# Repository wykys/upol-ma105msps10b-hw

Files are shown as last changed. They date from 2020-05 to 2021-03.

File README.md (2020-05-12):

# Multikanálový analyzátor 105 MSPS 10b

Vývoj hardware pro multikanálovou analýzu.

## Datasheets
Technická dokumentace používaná k vývoji.
### FPGA Xilinx 7 Series
- [Vivado Design Suite User Guide](https://www.xilinx.com/support/documentation/sw_manuals/xilinx2016_2/ug908-vivado-programming-debugging.pdf)
- [7 Series FPGAs Data Sheet: Overview](https://www.xilinx.com/support/documentation/data_sheets/ds180_7Series_Overview.pdf)
- [DC and AC Switching Characteristics](https://www.xilinx.com/support/documentation/data_sheets/ds189-spartan-7-data-sheet.pdf)
- [7 Series FPGAs Configuration User Guide](https://www.xilinx.com/support/documentation/user_guides/ug470_7Series_Config.pdf)
- [Using SPI Flash with 7 Series FPGAs](https://www.xilinx.com/support/documentation/application_notes/xapp586-spi-flash.pdf)
- [Spartan-7 FPGA Configuration with SPI Flash and Bank 14 at 1.35V](https://www.xilinx.com/support/documentation/application_notes/xapp1313-spartan-spi-config.pdf)
- [7 Series FPGAs SelectIO Resources User Guide](https://www.xilinx.com/support/documentation/user_guides/ug471_7Series_SelectIO.pdf)
- [7 Series FPGAs PCB Design Guide](https://www.xilinx.com/support/documentation/user_guides/ug483_7Series_PCB.pdf)
- [7 Series FPGAs Packaging and Pinout](https://www.xilinx.com/support/documentation/user_guides/ug475_7Series_Pkg_Pinout.pdf)

### Další dokumenty
- [Přehled logických obvodů ST](https://www.mouser.com/catalog/supplier/library/pdf/STLogic.pdf)
- [Zakončování LVCMOS](https://www.idt.com/eu/en/document/apn/953-quick-guide-output-terminations)
- [USB specifikace](https://www.silabs.com/documents/public/application-notes/AN0046.pdf)

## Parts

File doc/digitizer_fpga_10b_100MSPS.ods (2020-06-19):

Reference | Quantity | Value | Footprint | Datasheet | Link
C1 C2 C11 C12 C15 C16 C27 C28 C33 C35 C36 C45 C54 C57 C58 C61 C66 C78 C79 C80 C81 C83 C85 C86 C87 C98 C102 | 27 | 4u7 | Capacitor_SMD:C_0402_1005Metric | ~
C10 C19 C26 C43 C55 C63 C64 C65 C68 | 9 | 1u | Capacitor_SMD:C_0402_1005Metric | ~
C3 C4 C8 C9 C13 C14 C17 C18 C23 C24 C25 C32 C34 C37 C38 C39 C40 C41 C42 C44 C46 C47 C49 C50 C53 C56 C59 C60 C62 C67 C69 C70 C71 C72 C84 | 35 | 100n | Capacitor_SMD:C_0402_1005Metric | ~
C30 C31 | 2 | 2u2 | Capacitor_SMD:C_0402_1005Metric | ~
C5 C6 C20 C21 C48 C108 | 6 | 1n | Capacitor_SMD:C_0402_1005Metric | ~
C51 C52 | 2 | 47p | Capacitor_SMD:C_0402_1005Metric | ~
C7 C22 C29 | 3 | 47u/16V | Capacitor_Tantalum_SMD:CP_EIA-7343-31_Kemet-D | ~
C73 C74 C75 C76 C77 C82 C88 C93 | 8 | 47u | Capacitor_SMD:C_0402_1005Metric | ~
C89 C90 C91 C92 C94 C95 C96 C97 C99 C100 C101 C103 C104 C105 C106 C107 | 16 | 470n | Capacitor_SMD:C_0402_1005Metric | ~
D1 | 1 | AS3BJ-M3/52T | Diode_SMD:D_SMB | ~
D2 | 1 | PTVS3V3P1UP.115 | Diode_SMD:D_SOD-128 | ~
D3 D4 D5 D6 | 4 | BAT20JFILM | Diode_SMD:D_SOD-323 | ~
D7 D8 D9 D10 D11 D12 D13 D14 D15 | 9 | RED | LED_SMD:LED_0805_2012Metric | ~
FB1 | 1 | 742792515 | Inductor_SMD:L_1812_4532Metric | ~
J1 | 1 | POWER | Connector_Phoenix_MC:PhoenixContact_MC_1,5_2-G-3.5_1x02_P3.50mm_Horizontal | ~
J2 | 1 | SWD_01X06 | Connector_PinHeader_2.54mm:PinHeader_1x06_P2.54mm_Vertical | ~
J3 | 1 | DEBUG_SPI | Connector_PinHeader_2.54mm:PinHeader_2x04_P2.54mm_Vertical | ~
J4 | 1 | USB_B_Mini | Connector_USB:USB_Mini-B_Lumberg_2486_01_Horizontal | ~
J5 | 1 | SMA | Connector_Coaxial:SMA_Samtec_SMA-J-P-X-ST-EM1_EdgeMount | ~
J6 | 1 | JUMPER_DFS/GAIN | Connector_PinHeader_2.54mm:PinHeader_2x04_P2.54mm_Vertical | ~
J7 | 1 | DEBUG_FPGA_GPIO | Connector_PinHeader_2.54mm:PinHeader_2x04_P2.54mm_Vertical | ~
J8 | 1 | DIGILENT_JTAG_HS2_01X06 | Connector_PinHeader_2.54mm:PinHeader_1x06_P2.54mm_Vertical | https://reference.digilentinc.com/_media/jtag_hs2:jtag-hs2_rm.pdf
JP1 | 1 | Jumper_FTDI_RST | Connector_PinHeader_2.54mm:PinHeader_1x02_P2.54mm_Vertical | ~
L1 | 1 | ETQP3M6R8KVP | Inductor_SMD:L_Bourns_SRN6045TA | ~
R1 R3 R4 R5 R14 R20 R21 R45 R121 R122 | 10 | 10k | Resistor_SMD:R_0603_1608Metric | ~
R11 | 1 | 2k87 | Resistor_SMD:R_0603_1608Metric | ~
R15 R16 R17 R18 R125 R126 R127 R128 | 8 | 220R | Resistor_SMD:R_0603_1608Metric | ~
R19 R22 R23 R27 R28 R29 R30 R31 R32 R33 R34 R35 R36 R48 R49 R50 R51 R52 R53 R54 R55 R56 R57 R58 R59 R60 R61 R62 R63 R64 R65 R66 R67 R68 R69 R70 R71 R72 R73 R74 R75 R76 R77 R78 R79 R80 R81 R82 R83 R84 R85 R86 R87 R89 R90 R91 R92 R93 R94 R95 R96 R97 R98 R99 R100 R101 R102 R103 R104 R105 R106 R107 R108 R109 R110 R111 R112 R113 R114 R115 R116 R117 | 82 | 47R | Resistor_SMD:R_0402_1005Metric | ~
R2 | 1 | 3k9 | Resistor_SMD:R_0603_1608Metric | ~
R24 R25 R26 R43 R44 R118 R119 R120 R129 R130 | 10 | 4k7 | Resistor_SMD:R_0603_1608Metric | ~
R37 R38 R39 R41 | 4 | 56R2 | Resistor_SMD:R_0603_1608Metric | ~
R40 R42 R46 R47 | 4 | 301R | Resistor_SMD:R_0603_1608Metric | ~
R6 | 1 | 1k13 | Resistor_SMD:R_0603_1608Metric | ~
R7 | 1 | 4k53 | Resistor_SMD:R_0603_1608Metric | ~
R8 R10 R12 | 3 | 3k57 | Resistor_SMD:R_0603_1608Metric | ~
R88 R123 R124 | 3 | 1k | Resistor_SMD:R_0603_1608Metric | ~
R9 R13 | 2 | 1k15 | Resistor_SMD:R_0603_1608Metric | ~
SW1 | 1 | RST | Button_Switch_SMD:SW_SPST_CK_RS282G05A3 | ~
SW2 | 1 | PROG | Button_Switch_SMD:SW_SPST_CK_RS282G05A3 | ~
U1 | 1 | LM3880MF-1AA | Package_TO_SOT_SMD:SOT-23-6 | http://www.ti.com/lit/ds/symlink/lm3880.pdf | https://cz.mouser.com/ProductDetail/Texas-Instruments/LM3880MF-1AA?qs=QbsRYf82W3Fl%2Fq3cHZXlFw%3D%3D
U10 | 1 | ADA4930-1 | Package_CSP:LFCSP-16-1EP_3x3mm_P0.5mm_EP1.7x1.7mm | https://www.analog.com/media/en/technical-documentation/data-sheets/ADA4930-1_4930-2.pdf | https://cz.mouser.com/ProductDetail/Analog-Devices/ADA4930-1YCPZ-R7?qs=BpaRKvA4VqGLtX2TPWl0aQ%3D%3D
U11 | 1 | IS61WV12816EDBLL-10TLI | Package_SO:TSOP-II-44_10.16x18.41mm_P0.8mm | http://www.issi.com/WW/pdf/61-64WV12816EDBLL.pdf | https://cz.mouser.com/ProductDetail/ISSI/IS61WV12816EDBLL-10TLI?qs=9hm%252BDT1Jr7wdTeyW8VsKuw%3D%3D
U12 | 1 | TLV431ACDBZR | Package_TO_SOT_SMD:SOT-23 | http://www.ti.com/lit/ds/symlink/tl431.pdf | https://cz.mouser.com/ProductDetail/Texas-Instruments/TLV431ACDBZR?qs=m96fseALk3UFqurlruAFnw%3D%3D
U13 | 1 | AD9214-105 | Package_SO:SSOP-28_5.3x10.2mm_P0.65mm | https://www.analog.com/media/en/technical-documentation/data-sheets/AD9214.pdf | https://cz.mouser.com/ProductDetail/Analog-Devices/AD9214BRSZ-105?qs=%2FtpEQrCGXCwwKyKT%252BwKAAg%3D%3D
U14 | 1 | XC7S15-FTGB196 | Package_BGA:Xilinx_FTGB196 | https://www.xilinx.com/support/documentation/data_sheets/ds180_7Series_Overview.pdf | https://cz.mouser.com/ProductDetail/Xilinx/XC7S15-2FTGB196I?qs=unwgFEO1A6uXTG1xGkfbTw%3D%3D | zkontrolovat pouzdro
U15 | 1 | IS25LP064A-JKx | Package_SON:WSON-8-1EP_6x5mm_P1.27mm_EP3.4x4mm | http://www.issi.com/WW/pdf/25LP032-64A-B.pdf | https://cz.mouser.com/ProductDetail/ISSI/IS25LP064A-JKLE?qs=ULk7ZlyDR4fnjlhNymmuhQ%3D%3D
U2 U3 U4 U5 | 4 | NCP59744MN1 | Package_DFN_QFN:DFN-10-1EP_3x3mm_P0.5mm_EP1.7x2.5mm | https://www.onsemi.com/pub/Collateral/NCP59744-D.PDF | https://cz.mouser.com/ProductDetail/ON-Semiconductor/NCP59744MN1ADJTBG
U6 | 1 | STM32H750VBTx | Package_QFP:LQFP-100_14x14mm_P0.5mm | https://www.st.com/resource/en/datasheet/stm32h750ib.pdf | https://cz.mouser.com/ProductDetail/STMicroelectronics/STM32H750VBT6?qs=%252BEew9%252B0nqrBAeuu%2FsQQSzQ%3D%3D
U7 | 1 | USBLC6-2SC6 | Package_TO_SOT_SMD:SOT-23-6 | http://www2.st.com/resource/en/datasheet/CD00050750.pdf
U8 | 1 | SN74LVC1G11DCKR | Package_TO_SOT_SMD:SOT-363_SC-70-6 | http://www.ti.com/lit/sg/scyt129e/scyt129e.pdf
U9 | 1 | FT231XS | Package_SO:SSOP-20_3.9x8.7mm_P0.635mm | https://www.ftdichip.com/Support/Documents/DataSheets/ICs/DS_FT231X.pdf | https://cz.mouser.com/ProductDetail/FTDI/FT231XS-R?qs=Gp1Yz1mis3WduRPsgrTbtg%3D%3D
X1 | 1 | ASTX-H11-25.000MHZ-T | Oscillator:Oscillator_SMD_SeikoEpson_SG8002CE-4Pin_3.2x2.5mm | https://support.epson.biz/td/api/doc_check.php?dl=brief_SG5032CCN&lang=en
X2 | 1 | SIT8209AI-21-33S-100.000000X | Oscillator:Oscillator_SMD_SeikoEpson_SG8002CE-4Pin_3.2x2.5mm | https://support.epson.biz/td/api/doc_check.php?dl=brief_SG5032CCN&lang=en

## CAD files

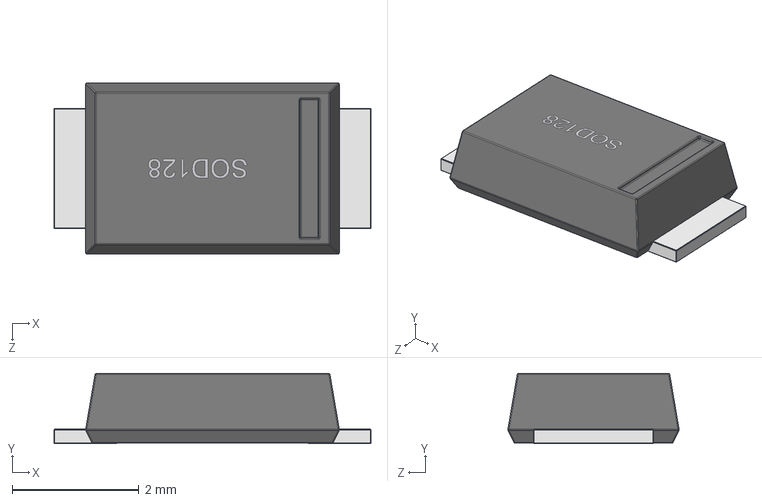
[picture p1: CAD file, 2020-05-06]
design/3D/SOD-128.step
5.00 x 1.11 x 2.70 mm

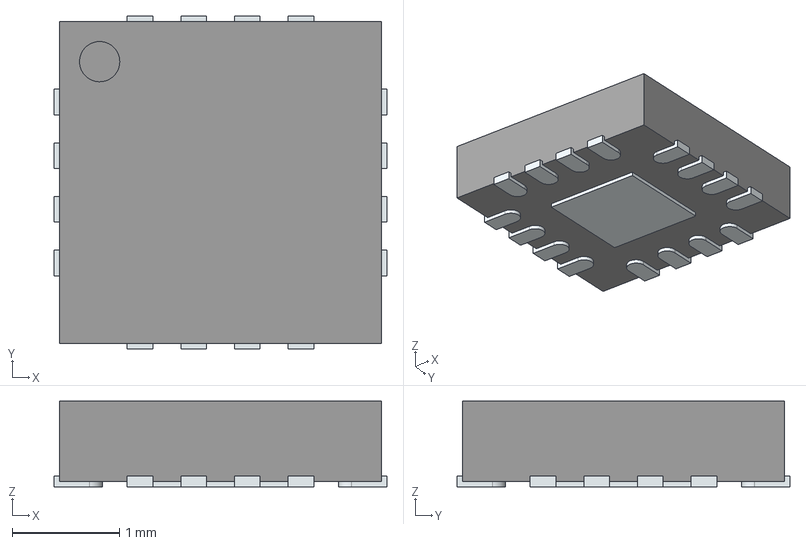
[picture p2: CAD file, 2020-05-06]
design/3D/ADA4930-1YCPZ-RL.stp
3.10 x 3.10 x 0.8 mm
ThermalPin
PinsArrayLR
PinsArrayTB

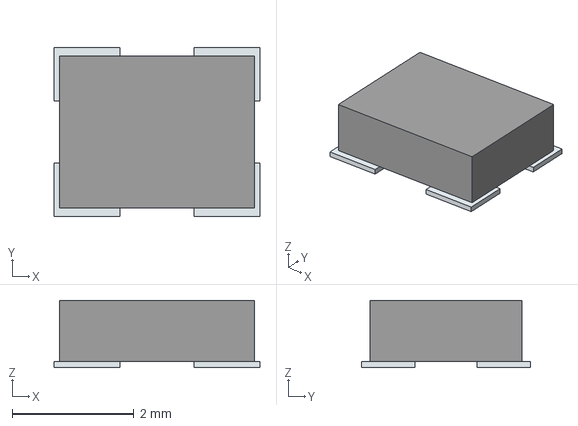
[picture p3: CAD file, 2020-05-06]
design/3D/ASTX-H11-25.000MHZ-T.stp
3.38 x 2.78 x 1.10 mm
Pins

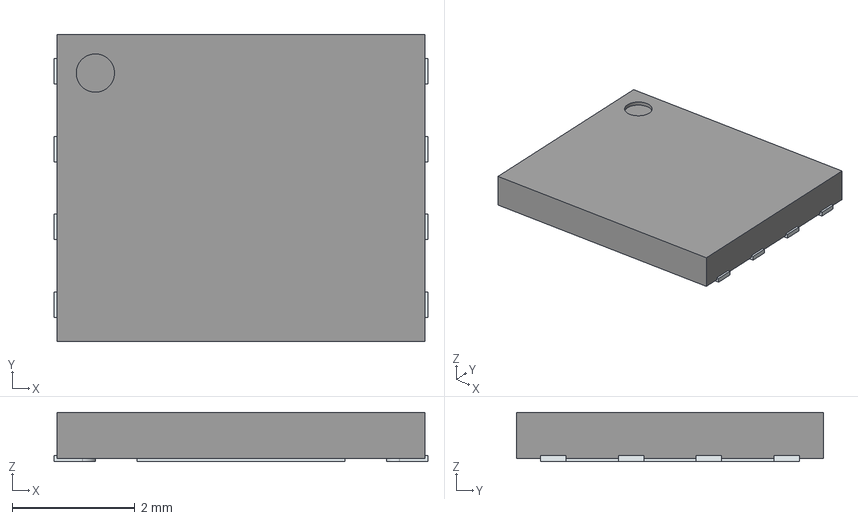
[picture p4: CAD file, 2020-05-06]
design/3D/IS25LP064A-JKLE.stp
6.10 x 5.00 x 0.8 mm
ThermalPin
PinsArrayLR

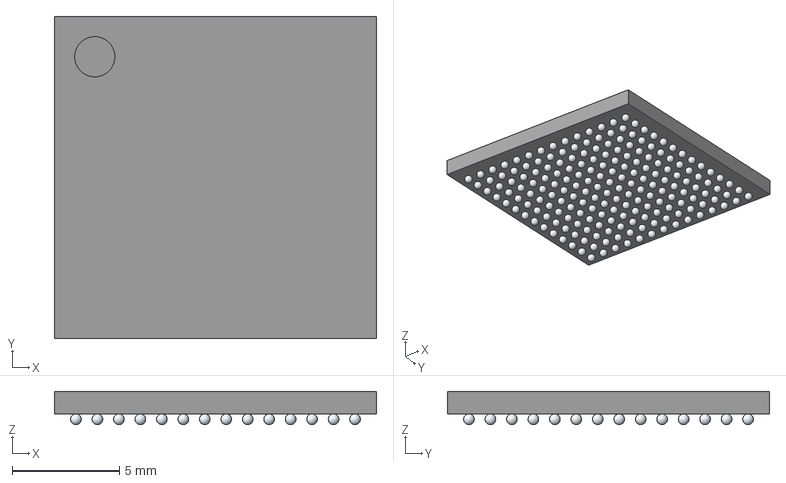
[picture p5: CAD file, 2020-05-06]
design/3D/XC7S15-2FTGB196I.stp
15.0 x 15.0 x 1.55 mm

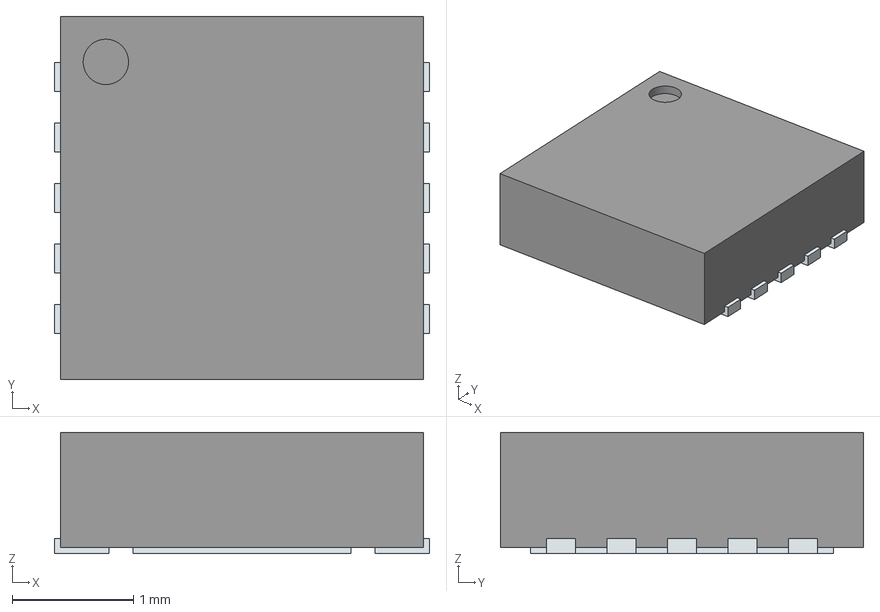
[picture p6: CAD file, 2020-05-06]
design/3D/NCP59744MN1ADJTBG.stp
3.10 x 3.00 x 1.00 mm
ThermalPin
PinsArrayLR

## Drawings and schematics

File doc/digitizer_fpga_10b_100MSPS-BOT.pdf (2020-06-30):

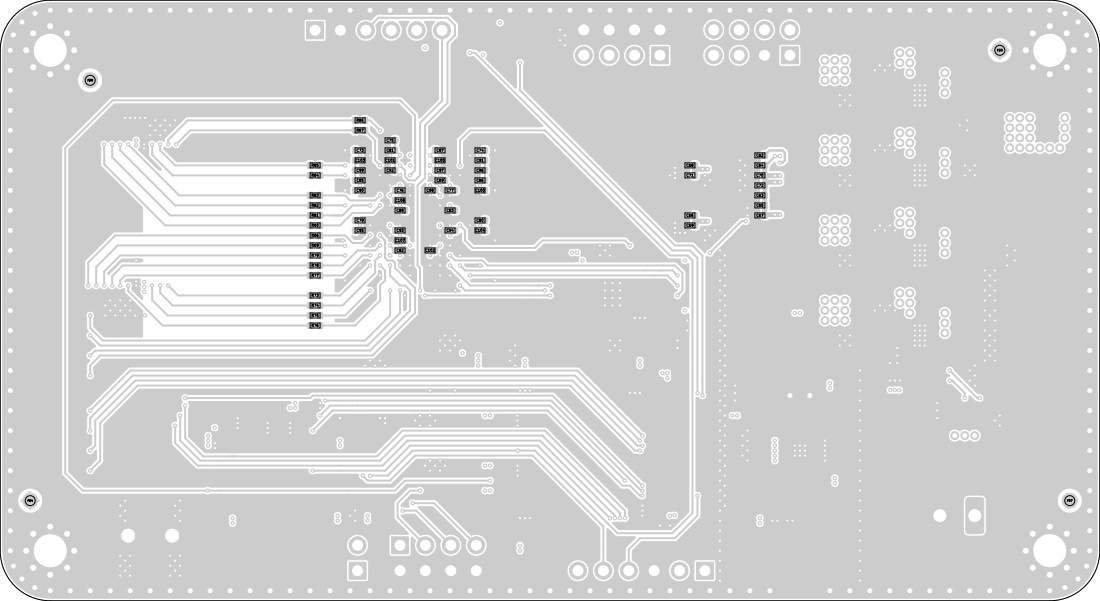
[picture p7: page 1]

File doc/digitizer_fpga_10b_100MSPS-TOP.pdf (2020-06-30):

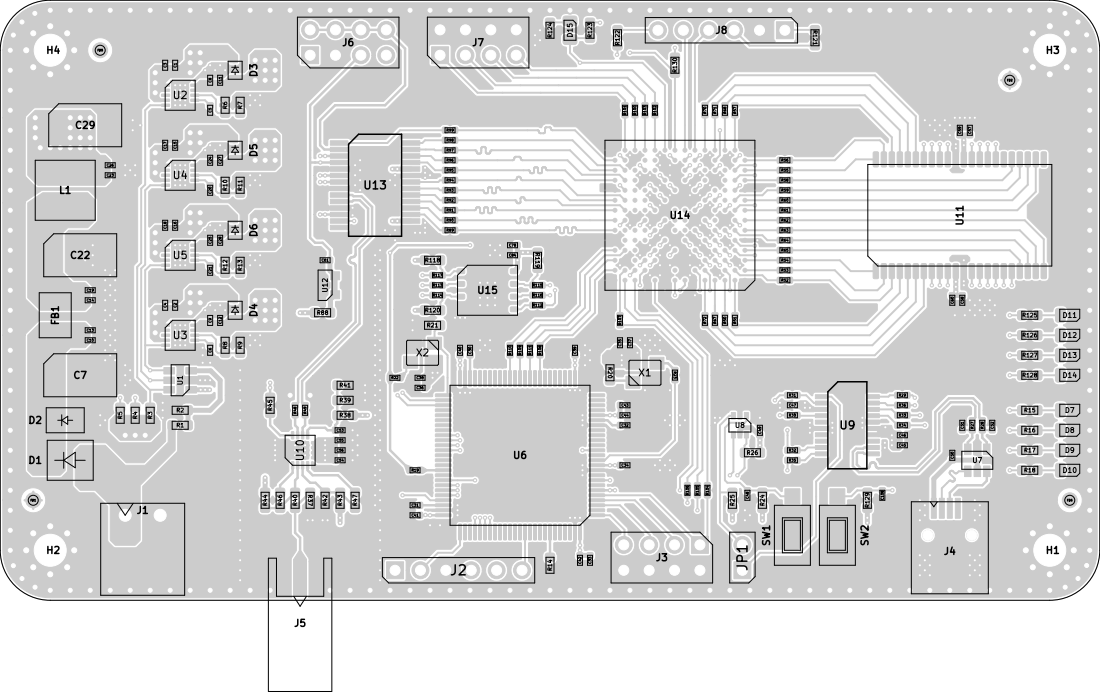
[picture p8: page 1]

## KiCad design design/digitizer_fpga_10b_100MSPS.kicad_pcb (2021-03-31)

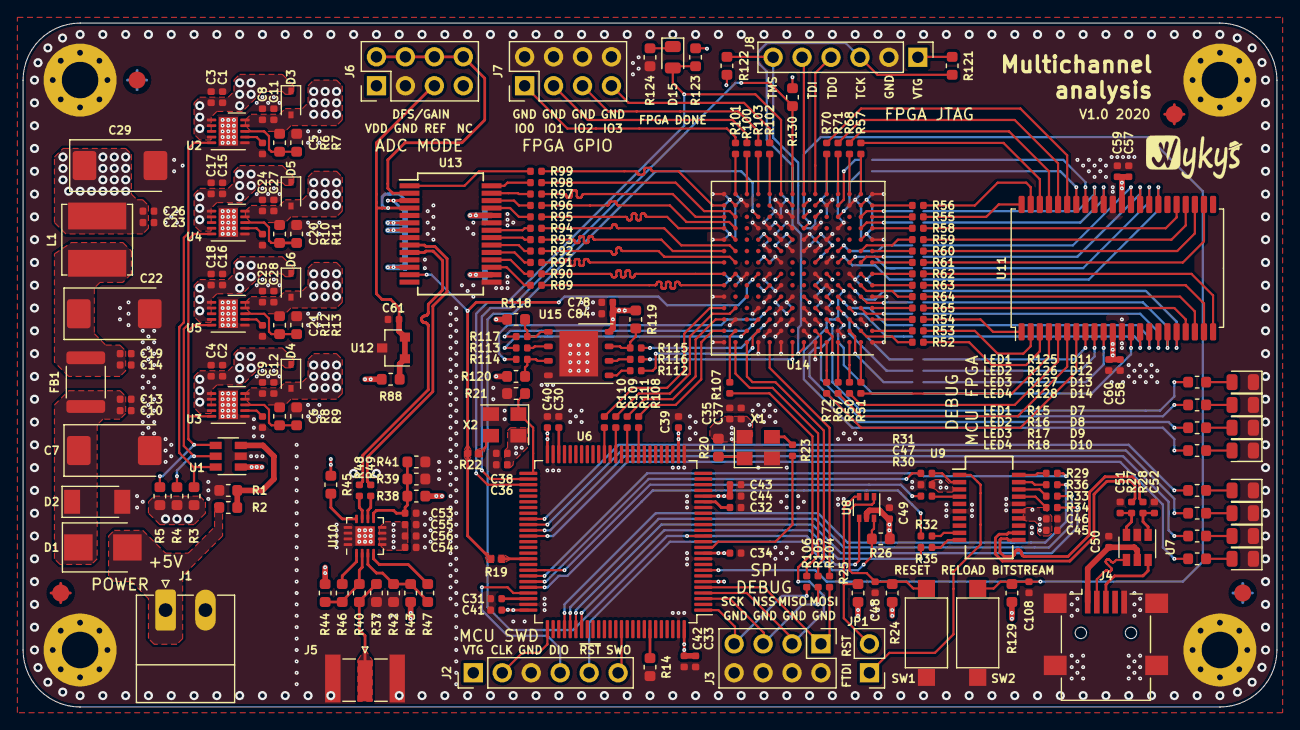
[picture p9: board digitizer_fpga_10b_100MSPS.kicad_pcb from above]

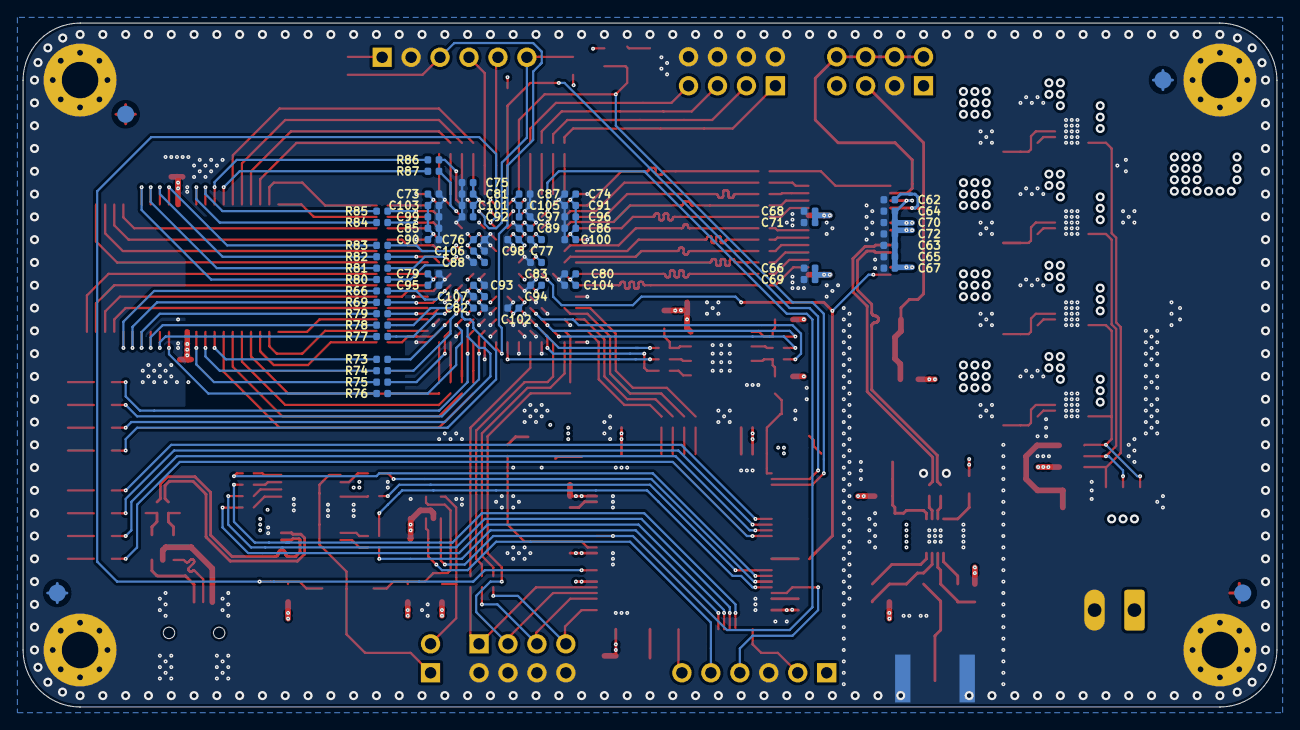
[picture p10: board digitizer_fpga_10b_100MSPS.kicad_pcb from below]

Board: 4 copper layers, 110.0 x 60.0 mm, 296 parts (65 on the bottom side), 234 nets.

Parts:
C1, C2, C11, C12, C15, C16, C27, C28, C33, C35, C36, C45, C54, C57, C58, C61, C66, C78, C79, C80, C81, C83, C85, C86, C87, C98, C102: 4u7; C_0402_1005Metric
C3, C4, C8, C9, C13, C14, C17, C18, C23, C24, C25, C32, C34, C37, C38, C39, C40, C41, C42, C44, C46, C47, C49, C50, C53, C56, C59, C60, C62, C67, C69, C70, C71, C72, C84: 100n; C_0402_1005Metric
C5, C6, C20, C21, C48, C108: 1n; C_0402_1005Metric
C7, C22, C29: 47u/16V; CP_EIA-7343-31_Kemet-D
C10, C19, C26, C43, C55, C63, C64, C65, C68: 1u; C_0402_1005Metric
C30, C31: 2u2; C_0402_1005Metric
C51, C52: 47p; C_0402_1005Metric
C73, C74, C75, C76, C77, C82, C88, C93: 47u; C_0402_1005Metric
C89, C90, C91, C92, C94, C95, C96, C97, C99, C100, C101, C103, C104, C105, C106, C107: 470n; C_0402_1005Metric
D1: AS3BJ-M3/52T; D_SMB
D2: PTVS3V3P1UP.115; D_SOD-128
D3, D4, D5, D6: BAT20JFILM; D_SOD-323
D7, D8, D9, D10, D11, D12, D13, D14, D15: RED; LED_0805_2012Metric
FB1: 742792515; L_1812_4532Metric
FD1, FD2: Fiducial cu top; Fiducial_Pad_1.5mm_Outer_2.5mm
FD3, FD4: Fiducial cu bot; Fiducial_Pad_1.5mm_Outer_2.5mm
FD5, FD6: Fiducial paste top; Fiducial_Paste_Pad_1.5mm_Outer_2.5mm
FD7, FD8: Fiducial paste bot; Fiducial_Paste_Pad_1.5mm_Outer_2.5mm
GR1: Wykys; wykys_small_skill
H1, H2, H3, H4: HOLE_3.2MM; MountingHole_3.2mm_M3_Pad_Via
J1: POWER; PhoenixContact_MC_1,5_2-G-3.5_1x02_P3.50mm_Horizontal
J2: SWD_01X06; PinHeader_1x06_P2.54mm_Vertical
J3: DEBUG_SPI; PinHeader_2x04_P2.54mm_Vertical
J4: USB_B_Mini; USB_Mini-B_Lumberg_2486_01_Horizontal
J5: SMA; SMA_Samtec_SMA-J-P-X-ST-EM1_EdgeMount
J6: JUMPER_DFS/GAIN; PinHeader_2x04_P2.54mm_Vertical
J7: DEBUG_FPGA_GPIO; PinHeader_2x04_P2.54mm_Vertical
J8: DIGILENT_JTAG_HS2_01X06; PinHeader_1x06_P2.54mm_Vertical
JP1: Jumper_FTDI_RST; PinHeader_1x02_P2.54mm_Vertical
L1: ETQP3M6R8KVP; L_Bourns_SRN6045TA
R1, R3, R4, R5, R14, R20, R21, R45, R121, R122: 10k; R_0603_1608Metric
R2: 3k9; R_0603_1608Metric
R6: 1k13; R_0603_1608Metric
R7: 4k53; R_0603_1608Metric
R8, R10, R12: 3k57; R_0603_1608Metric
R9, R13: 1k15; R_0603_1608Metric
R11: 2k87; R_0603_1608Metric
R15, R16, R17, R18, R125, R126, R127, R128: 220R; R_0603_1608Metric
R19, R22, R23, R27, R28, R29, R30, R31, R32, R33, R34, R35, R36, R48, R49, R50, R51, R52, R53, R54, R55, R56, R57, R58, R59, R60, R61, R62, R63, R64, R65, R66, R67, R68, R69, R70, R71, R72, R73, R74, R75, R76, R77, R78, R79, R80, R81, R82, R83, R84, R85, R86, R87, R89, R90, R91, R92, R93, R94, R95, R96, R97, R98, R99, R100, R101, R102, R103, R104, R105, R106, R107, R108, R109, R110, R111, R112, R113, R114, R115, R116, R117: 47R; R_0402_1005Metric
R24, R25, R26, R43, R44, R118, R119, R120, R129, R130: 4k7; R_0603_1608Metric
R37, R38, R39, R41: 56R2; R_0603_1608Metric
R40, R42, R46, R47: 301R; R_0603_1608Metric
R88, R123, R124: 1k; R_0603_1608Metric
SW1: RST; SW_SPST_CK_RS282G05A3
SW2: PROG; SW_SPST_CK_RS282G05A3
U1: LM3880MF-1AA; SOT-23-6
U2, U3, U4, U5: NCP59744MN1; DFN-10-1EP_3x3mm_P0.5mm_EP1.7x2.5mm
U6: STM32H750VBTx; LQFP-100_14x14mm_P0.5mm
U7: USBLC6-2SC6; SOT-23-6
U8: SN74LVC1G11DCKR; SOT-363_SC-70-6
U9: FT231XS; SSOP-20_3.9x8.7mm_P0.635mm
U10: ADA4930-1; LFCSP-16-1EP_3x3mm_P0.5mm_EP1.7x1.7mm
U11: IS61WV12816EDBLL-10TLI; TSOP-II-44_10.16x18.41mm_P0.8mm
U12: TLV431ACDBZR; SOT-23
U13: AD9214; SSOP-28_5.3x10.2mm_P0.65mm
U14: XC7S15-FTGB196; Xilinx_FTGB196
U15: IS25LP064A-JKx; WSON-8-1EP_6x5mm_P1.27mm_EP3.4x4mm
X1: ASTX-H11-25.000MHZ-T; Oscillator_SMD_SeikoEpson_SG8002CE-4Pin_3.2x2.5mm
X2: SIT8209AI-21-33S-100.000000X; Oscillator_SMD_SeikoEpson_SG8002CE-4Pin_3.2x2.5mm

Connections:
+1V0: C8.1, C11.1, C76.1, C82.1, C88.1, C93.1, C98.1, C102.1, C106.1, C107.1, D3.2 (A), R6.1, U2.9 (OUT), U2.10 (OUT), U14.D6 (VCCINT), U14.D8 (VCCINT), U14.E5 (VCCBRAM), U14.E7 (VCCINT), U14.E9 (VCCINT), U14.F6 (VCCINT), U14.G5 (VCCBRAM), U14.G9 (VCCINT), U14.H6 (VCCINT), U14.J5 (VCCBRAM), U14.J9 (VCCINT), U14.K6 (VCCINT), U14.K8 (VCCINT)
+1V8: C24.1, C27.1, C77.1, C83.1, C89.1, C94.1, D5.2 (A), R10.1, U4.9 (OUT), U4.10 (OUT), U14.F10 (VCCAUX), U14.H10 (VCCAUX), U14.K10 (VCCAUX), U14.L9 (VCCAUX)
+3V3A: C9.1, C12.1, C54.1, C55.1, C56.1, C63.1, C64.1, C65.1, C67.1, C70.1, C72.1, D4.2 (A), R8.1, R38.1, R43.1, R44.1, R45.1, R88.1, U3.9 (OUT), U3.10 (OUT), U10.5 (+VS), U10.6 (+VS), U10.7 (+VS), U10.8 (+VS), U13.3 (REFSEANSE), U13.6 (AVDD), U13.7 (AVDD), U13.12 (AVDD)
+3V3D: C25.1, C28.1, C33.1, C34.1, C35.1, C36.1, C37.1, C38.1, C39.1, C40.1, C41.1, C42.1, C43.1, C44.1, C45.1, C46.1, C47.1, C49.1, C57.1, C58.1, C59.1, C60.1, C66.1, C68.1, C69.1, C71.1, C73.1, C74.1, C75.1, C78.1, C79.1, C80.1, C81.1, C84.1, C85.1, C86.1, C87.1, C90.1, C91.1, C92.1, C95.1, C96.1, C97.1, C99.1, C100.1, C101.1, C103.1, C104.1, C105.1, D6.2 (A), J2.1 (VTG), J6.1, J8.1 (VTG), R12.1, R20.1, R24.1, R25.1, R26.1, R118.1, R119.1, R120.1, R121.1, R122.1, R123.1, R129.1, R130.1, U5.9 (OUT), U5.10 (OUT), U6.6 (VBAT), U6.11 (VDD), U6.21 (VDDA), U6.27 (VDD), U6.50 (VDD), U6.75 (VDD), U6.100 (VDD), U8.5 (VCC), U9.3 (VCCIO), U9.14 (~RESET), U9.15 (VCC), U11.11 (VDD), U11.33 (VDD), U13.16 (DVDD), U13.24 (DVDD), U14.G2 (VCCO_34), U14.G13 (VCCO_14), U14.K2 (VCCO_34), U14.K13 (VCCO_14), U14.M7 (M0_0), U14.N2 (VCCO_34), U14.N6 (VCCO_0), U14.N7 (CFGBVS_0), U14.N8 (VCCO_0), U14.N13 (VCCO_14), U15.8 (VCC), X1.4 (Vcc), X2.4 (Vcc)
+5V: D1.2 (A), J1.1, R1.1
/ADC/ADC_DATA0: R89.2, U14.F14 (IO_L9N_T1_DQS_D13_14)
/ADC/ADC_DATA1: R90.2, U14.G14 (IO_L9P_T1_DQS_14)
/ADC/ADC_DATA2: R91.2, U14.H14 (IO_L14N_T2_SRCC_14)
/ADC/ADC_DATA3: R92.2, U14.H13 (IO_L14P_T2_SRCC_14)
/ADC/ADC_DATA4: R93.2, U14.J14 (IO_L18N_T2_D27_14)
/ADC/ADC_DATA5: R94.2, U14.J13 (IO_L18P_T2_D28_14)
/ADC/ADC_DATA6: R95.2, U14.L14 (IO_L15N_T2_DQS_DOUT_CSO_B_14)
/ADC/ADC_DATA7: R96.2, U14.L13 (IO_L16N_T2_D31_14)
/ADC/ADC_DATA8: R97.2, U14.M14 (IO_L21N_T3_DQS_D22_14)
/ADC/ADC_DATA9: R98.2, U14.M13 (IO_L15P_T2_DQS_RDWR_B_14)
/ADC/ADC_OVRNG: R99.2, U14.N14 (IO_L21P_T3_DQS_14)
/ADC/CLK: R19.2, R22.1, U13.13 (ENCODE), U14.G11 (IO_L12P_T1_MRCC_14)
/ADC/D0: R89.1, U13.17 (D0)
/ADC/D1: R90.1, U13.18 (D1)
/ADC/D2: R91.1, U13.19 (D2)
/ADC/D3: R92.1, U13.20 (D3)
/ADC/D4: R93.1, U13.21 (D4)
/ADC/D5: R94.1, U13.22 (D5)
/ADC/D6: R95.1, U13.25 (D6)
/ADC/D7: R96.1, U13.26 (D7)
/ADC/D8: R97.1, U13.27 (D8)
/ADC/D9: R98.1, U13.28 (D9)
/ADC/IN+: R49.1, U13.9 (AIN)
/ADC/IN-: R48.1, U13.10 (~AIN)
/ADC/OR: R99.1, U13.1 (OR)
/ADC/REF: C61.1, C62.1, J6.5, R88.2, U12.1 (K), U12.2 (REF), U13.4 (REF)
/FPGA/BRIDGE_MISO: J3.3, R107.1, U6.4 (PE5)
/FPGA/BRIDGE_MOSI: J3.1, R104.1, U6.5 (PE6)
/FPGA/BRIDGE_NSS: J3.5, R105.1, U6.3 (PE4)
/FPGA/BRIDGE_NU0: R108.1, U6.34 (PB0)
/FPGA/BRIDGE_NU1: R111.1, U6.36 (PB2)
/FPGA/BRIDGE_NU2: R109.1, U6.38 (PE8)
/FPGA/BRIDGE_NU3: R110.1, U6.40 (PE10)
/FPGA/BRIDGE_SCK: J3.7, R106.1, U6.1 (PE2)
/FPGA/DEBUG_GPIO_0: J7.1, R101.1
/FPGA/DEBUG_GPIO_1: J7.3, R100.1
/FPGA/DEBUG_GPIO_2: J7.5, R103.1
/FPGA/DEBUG_GPIO_3: J7.7, R102.1
/FPGA/DEBUG_LED1: R125.2, U14.B5 (IO_L4P_T0_34)
/FPGA/DEBUG_LED2: R126.2, U14.B6 (IO_0_34)
/FPGA/DEBUG_LED3: R127.2, U14.C5 (IO_L6P_T0_34)
/FPGA/DEBUG_LED4: R128.2, U14.F4 (IO_L12N_T1_MRCC_34)
/FPGA/FPGA_CCLK: R116.1, U14.A8 (CCLK_0)
/FPGA/FPGA_DONE: D15.2 (A), R123.2, U6.53 (PB14), U14.P9 (DONE_0)
/FPGA/FPGA_DQ0: R112.1, U14.B11 (IO_L1P_T0_D00_MOSI_14)
/FPGA/FPGA_DQ1: R113.1, U14.B12 (IO_L1N_T0_D01_DIN_14)
/FPGA/FPGA_DQ2: R114.1, U14.D10 (IO_L2P_T0_D02_14)
/FPGA/FPGA_DQ3: R115.1, U14.C10 (IO_L2N_T0_D03_14)
/FPGA/FPGA_ERROR: R130.2, U6.52 (PB13), U14.P8 (INIT_B_0)
/FPGA/FPGA_FCS_B: R117.1, U14.C11 (IO_L6P_T0_FCS_B_14)
/FPGA/FPGA_LOAD_BITSTREAM: C108.1, R129.2, SW2.2, U6.8 (PC14), U14.L7 (PROGRAM_B_0)
/FPGA/SRAM_A0: R50.1, U14.A3 (IO_L2N_T0_34)
/FPGA/SRAM_A1: R51.1, U14.A2 (IO_L3N_T0_DQS_34)
/FPGA/SRAM_A2: R52.1, U14.B2 (IO_L5P_T0_34)
/FPGA/SRAM_A3: R53.1, U14.B1 (IO_L5N_T0_34)
/FPGA/SRAM_A4: R54.1, U14.C1 (IO_L11N_T1_SRCC_34)
/FPGA/SRAM_A5: R55.1, U14.M1 (IO_L18P_T2_34)
/FPGA/SRAM_A6: R56.1, U14.N1 (IO_L20N_T3_34)
/FPGA/SRAM_A7: R57.1, U14.P2 (IO_L20P_T3_34)
/FPGA/SRAM_A8: R58.1, U14.L1 (IO_L18N_T2_34)
/FPGA/SRAM_A9: R59.1, U14.J2 (IO_L15P_T2_DQS_34)
/FPGA/SRAM_A10: R60.1, U14.J1 (IO_L15N_T2_DQS_34)
/FPGA/SRAM_A11: R61.1, U14.H1 (IO_L14N_T2_SRCC_34)
/FPGA/SRAM_A12: R62.1, U14.G1 (IO_L9P_T1_DQS_34)
/FPGA/SRAM_A13: R63.1, U14.F1 (IO_L9N_T1_DQS_34)
/FPGA/SRAM_A14: R64.1, U14.F2 (IO_L8N_T1_34)
/FPGA/SRAM_A15: R65.1, U14.D1 (IO_L11P_T1_SRCC_34)
/FPGA/SRAM_A16: R66.1, U14.F3 (IO_L8P_T1_34)
/FPGA/SRAM_IO0: R72.2, U14.A5 (IO_L4N_T0_34)
/FPGA/SRAM_IO1: R73.2, U14.C3 (IO_L1N_T0_34)
/FPGA/SRAM_IO2: R74.2, U14.D4 (IO_L7N_T1_34)
/FPGA/SRAM_IO3: R75.2, U14.B3 (IO_L3P_T0_DQS_34)
/FPGA/SRAM_IO4: R76.2, U14.C4 (IO_L6N_T0_VREF_34)
/FPGA/SRAM_IO5: R77.2, U14.D3 (IO_L1P_T0_34)
/FPGA/SRAM_IO6: R78.2, U14.E4 (IO_L7P_T1_34)
/FPGA/SRAM_IO7: R79.2, U14.D2 (IO_L10N_T1_34)
/FPGA/SRAM_IO8: R80.2, U14.H4 (IO_L13P_T2_MRCC_34)
/FPGA/SRAM_IO9: R81.2, U14.H3 (IO_L13N_T2_MRCC_34)
/FPGA/SRAM_IO10: R82.2, U14.H2 (IO_L14P_T2_SRCC_34)
/FPGA/SRAM_IO11: R83.2, U14.J4 (IO_L17P_T2_34)
/FPGA/SRAM_IO12: R84.2, U14.L2 (IO_L22N_T3_34)
/FPGA/SRAM_IO13: R85.2, U14.M2 (IO_L19N_T3_VREF_34)
/FPGA/SRAM_IO14: R86.2, U14.N4 (IO_L24N_T3_34)
/FPGA/SRAM_IO15: R87.2, U14.M4 (IO_L23N_T3_34)
/FPGA/TCK: J8.3 (TCK), R121.2, U14.A7 (TCK_0)
/FPGA/TDI: J8.5 (TDI), U14.P7 (TDI_0)
/FPGA/TDO: J8.4 (TDO), U14.P6 (TDO_0)
/FPGA/TMS: J8.6 (TMS), R122.2, U14.M6 (TMS_0)
/FPGA/~RST: U6.14 (NRST), U8.4, U14.M11 (IO_L20P_T3_D24_14)
/FPGA/~SRAM_CE: R67.1, U14.A4 (IO_L2P_T0_34)
/FPGA/~SRAM_LB: R70.1, U14.P5 (IO_L24P_T3_34)
/FPGA/~SRAM_OE: R68.1, U14.P3 (IO_L21N_T3_DQS_34)
/FPGA/~SRAM_UB: R71.1, U14.P4 (IO_L21P_T3_DQS_34)
/FPGA/~SRAM_WE: R69.1, U14.E2 (IO_L10P_T1_34)
/LNA/IN: J5.1 (In), R37.1, R40.2
/MCU/DEBUG_LED1: R15.2, U6.59 (PD12)
/MCU/DEBUG_LED2: R16.2, U6.60 (PD13)
/MCU/DEBUG_LED3: R17.2, U6.61 (PD14)
/MCU/DEBUG_LED4: R18.2, U6.62 (PD15)
/MCU/FTDI_CBUS0: R33.2, U6.80 (PC12)
/MCU/FTDI_CBUS1: R34.2, U6.81 (PD0)
/MCU/FTDI_CBUS2: R35.2, U6.82 (PD1)
/MCU/FTDI_CBUS3: R36.2, U6.79 (PC11)
/MCU/FTDI_RX: R30.2, U6.68 (PA9)
/MCU/FTDI_TX: R29.2, U6.69 (PA10)
/MCU/MCU_OSC_IN: R23.2, U6.12 (PH0)
/MCU/OSC: R22.2, X2.3 (OUT)
/MCU/OSC_OE: R21.1, U6.51 (PB12), X2.1 (OE)
/MCU/RCC_MCO2: R19.1, U6.66 (PC9)
/MCU/SWCLK: J2.2 (SWCLK), U6.76 (PA14)
/MCU/SWDIO: J2.4 (SWDIO), U6.72 (PA13)
/MCU/SWO: J2.6 (SWO), U6.89 (PB3)
/MCU/~FTDI_CTS: R32.2, U6.71 (PA12)
/MCU/~FTDI_RTS: R31.2, U6.70 (PA11)
/MCU/~PROG_RST: J2.5 (~RST), R26.2, U8.6
/Power/EN_1V0: R3.2, U1.6 (FLAG1), U2.5 (EN)
/Power/EN_1V8: R4.2, U1.5 (FLAG2), U4.5 (EN)
/Power/EN_3V3: R5.2, U1.4 (FLAG3), U3.5 (EN), U5.5 (EN)
/Power/VCC_FILTER_A: C7.1, C10.1, C13.1, D1.1 (K), D2.1 (K), FB1.2
/Power/VCC_FILTER_B: C14.1, C19.1, C22.1, FB1.1, L1.1
/USB/D+: R28.2, U9.11 (USBDP)
/USB/D-: R27.2, U9.12 (USBDM)
/USB/DATA+: C52.1, R28.1, U7.1 (IO1)
/USB/DATA-: C51.1, R27.1, U7.3 (IO2)
/USB/USB+: J4.3 (D+), U7.6 (IO1)
/USB/USB-: J4.2 (D-), U7.4 (IO2)
/USB/VBUS: C50.1, J4.1 (VBUS), U7.5 (VBUS)
/USB/~BTN_RST: C48.1, R24.2, SW1.2, U8.1
/USB/~FTDI_RST: JP1.1, U9.1 (~DTR)
GND: C1.2, C2.2, C3.2, C4.2, C5.2, C6.2, C7.2, C8.2, C9.2, C10.2, C11.2, C12.2, C13.2, C14.2, C15.2, C16.2, C17.2, C18.2, C19.2, C20.2, C21.2, C22.2, C23.2, C24.2, C25.2, C26.2, C27.2, C28.2, C29.2, C30.2, C31.2, C32.2, C33.2, C34.2, C35.2, C36.2, C37.2, C38.2, C39.2, C40.2, C41.2, C42.2, C43.2, C44.2, C45.2, C46.2, C47.2, C48.2, C49.2, C50.2, C51.2, C52.2, C53.2, C54.2, C55.2, C56.2, C57.2, C58.2, C59.2, C60.2, C61.2, C62.2, C63.2, C64.2, C65.2, C66.2, C67.2, C68.2, C69.2, C70.2, C71.2, C72.2, C73.2, C74.2, C75.2, C76.2, C77.2, C78.2, C79.2, C80.2, C81.2, C82.2, C83.2, C84.2, C85.2, C86.2, C87.2, C88.2, C89.2, C90.2, C91.2, C92.2, C93.2, C94.2, C95.2, C96.2, C97.2, C98.2, C99.2, C100.2, C101.2, C102.2, C103.2, C104.2, C105.2, C106.2, C107.2, C108.2, D2.2 (A), D7.1 (K), D8.1 (K), D9.1 (K), D10.1 (K), D11.1 (K), D12.1 (K), D13.1 (K), D14.1 (K), H1.1, H2.1, H3.1, H4.1, J1.2, J2.3 (GND), J3.2, J3.4, J3.6, J3.8, J4.5 (GND), J4.6 (Shield), J5.2 (Ext), J6.3, J7.2, J7.4, J7.6, J7.8, J8.2 (GND), R2.2, R7.2, R9.2, R11.2, R13.2, R14.2, R21.2, R37.2, R39.2, R41.2, R42.2, R124.2, SW1.1, SW2.1, U1.2 (GND), U2.6 (GND), U2.11 (EP), U3.6 (GND), U3.11 (EP), U4.6 (GND), U4.11 (EP), U5.6 (GND), U5.11 (EP), U6.10 (VSS), U6.19 (VSSA), U6.26 (VSS), U6.49 (VSS), U6.74 (VSS), U6.99 (VSS), U7.2 (GND), U8.2 (GND), U9.6 (GND), U9.16 (GND), U10.13 (-VS), U10.14 (-VS), U10.15 (-VS), U10.16 (-VS), U10.17 (-VS), U11.12 (GND), U11.34 (GND), U12.3 (A), U13.5 (AGND), U13.8 (AGND), U13.11 (AGND), U13.15 (DGND), U13.23 (DGND), U14.A1 (GND), U14.A6 (GND), U14.A9 (GND), U14.A11 (GND), U14.A14 (GND), U14.B4 (GND), U14.B7 (GND), U14.B9 (GND), U14.B10 (IO_L3P_T0_DQS_PUDC_B_14), U14.C2 (GND), U14.C6 (GND), U14.C7 (GND), U14.C8 (GND), U14.C9 (GND), U14.C13 (GND), U14.D5 (GND), U14.D7 (GND), U14.D9 (GND), U14.D11 (GND), U14.E1 (GND), U14.E3 (GND), U14.E6 (GND), U14.E8 (GND), U14.E10 (GND), U14.E14 (GND), U14.F5 (GND), U14.F9 (GND), U14.G3 (GND), U14.G6 (GND), U14.G10 (GND), U14.G12 (GND), U14.H5 (GND), U14.H9 (GND), U14.J6 (GND), U14.J7 (DXN_0), U14.J8 (DXP_0), U14.J10 (GND), U14.K1 (GND), U14.K5 (GND), U14.K7 (GND), U14.K9 (GND), U14.K14 (GND), U14.L4 (GND), U14.L6 (GND), U14.L8 (GND), U14.L10 (GND), U14.L11 (GND), U14.M8 (M1_0), U14.M9 (M2_0), U14.N3 (GND), U14.N5 (GND), U14.N9 (GND), U14.N12 (GND), U14.P1 (GND), U14.P14 (GND), U15.4 (GND), U15.9 (GND), X1.2 (GND), X2.2 (GND)
IN: C1.1, C2.1, C3.1, C4.1, C15.1, C16.1, C17.1, C18.1, C23.1, C26.1, C29.1, D3.1 (K), D4.1 (K), D5.1 (K), D6.1 (K), L1.2, R3.1, R4.1, R5.1, U1.1 (VCC), U2.1 (IN), U2.2 (IN), U2.4 (BIAS), U3.1 (IN), U3.2 (IN), U3.4 (BIAS), U4.1 (IN), U4.2 (IN), U4.4 (BIAS), U5.1 (IN), U5.2 (IN), U5.4 (BIAS)
unnamed: C5.1, U2.7 (SS)
unnamed: C6.1, U3.7 (SS)
unnamed: C20.1, U4.7 (SS)
unnamed: C21.1, U5.7 (SS)
unnamed: C30.1, U6.48 (VCAP1)
unnamed: C31.1, U6.73 (VCAP2)
unnamed: C32.1, U6.20 (VREF+)
unnamed: C53.1, R38.2, R39.1, R41.1, U10.9 (VOCM)
unnamed: D7.2 (A), R15.1
unnamed: D8.2 (A), R16.1
unnamed: D9.2 (A), R17.1
unnamed: D10.2 (A), R18.1
unnamed: D11.2 (A), R125.1
unnamed: D12.2 (A), R126.1
unnamed: D13.2 (A), R127.1
unnamed: D14.2 (A), R128.1
unnamed: D15.1 (K), R124.1
unnamed: J6.2, J6.4, J6.6, J6.8, U13.2 (DFS/GAIN)
unnamed: JP1.2, R25.2, U8.3
unnamed: R1.2, R2.1, U1.3 (EN)
unnamed: R6.2, R7.1, U2.8 (FB)
unnamed: R8.2, R9.1, U3.8 (FB)
unnamed: R10.2, R11.1, U4.8 (FB)
unnamed: R12.2, R13.1, U5.8 (FB)
unnamed: R14.1, U6.94 (BOOT0)
unnamed: R20.2, X1.1 (OE)
unnamed: R23.1, X1.3 (OUT)
unnamed: R29.1, U9.20 (TXD)
unnamed: R30.1, U9.4 (RXD)
unnamed: R31.1, U9.2 (~RTS)
unnamed: R32.1, U9.9 (~CTS)
unnamed: R33.1, U9.18 (CBUS0)
unnamed: R34.1, U9.17 (CBUS1)
unnamed: R35.1, U9.10 (CBUS2)
unnamed: R36.1, U9.19 (CBUS3)
unnamed: R40.1, R44.2, R46.2, U10.2 (+IN)
unnamed: R42.1, R43.2, R47.2, U10.3 (-IN)
unnamed: R45.2, U10.12 (~PD)
unnamed: R46.1, U10.1 (-FB)
unnamed: R47.1, U10.4 (+FB)
unnamed: R48.2, U10.11 (-OUT)
unnamed: R49.2, U10.10 (+OUT)
unnamed: R50.2, U11.5 (A0)
unnamed: R51.2, U11.4 (A1)
unnamed: R52.2, U11.3 (A2)
unnamed: R53.2, U11.2 (A3)
unnamed: R54.2, U11.1 (A4)
unnamed: R55.2, U11.44 (A5)
unnamed: R56.2, U11.43 (A6)
unnamed: R57.2, U11.42 (A7)
unnamed: R58.2, U11.27 (A8)
unnamed: R59.2, U11.26 (A9)
unnamed: R60.2, U11.25 (A10)
unnamed: R61.2, U11.24 (A11)
unnamed: R62.2, U11.22 (A12)
unnamed: R63.2, U11.21 (A13)
unnamed: R64.2, U11.20 (A14)
unnamed: R65.2, U11.19 (A15)
unnamed: R66.2, U11.18 (A16)
unnamed: R67.2, U11.6 (~CE)
unnamed: R68.2, U11.41 (~OE)
unnamed: R69.2, U11.17 (~WE)
unnamed: R70.2, U11.39 (~LB)
unnamed: R71.2, U11.40 (~UB)
unnamed: R72.1, U11.7 (IO0)
unnamed: R73.1, U11.8 (IO1)
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

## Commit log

2020-05-06 Added design from old repository
    [ADA4930-1YCPZ-RL.stp, ASTX-H11-25.000MHZ-T.stp, IS25LP064A-JKLE.stp, NCP59744MN1ADJTBG.stp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]
2020-05-06 Added LAN placement
    [digitizer_fpga_10b_100MSPS.kicad_pcb]
2020-05-06 Added ADC placement
    [adc.kicad_sch, digitizer_fpga_10b_100MSPS.kicad_pcb, digitizer_fpga_10b_100MSPS.kicad_sch, fpga.kicad_sch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]
2020-05-06 Fixed LNA power
    [adc.kicad_sch, digitizer_fpga_10b_100MSPS.kicad_pcb, digitizer_fpga_10b_100MSPS.kicad_sch, fpga.kicad_sch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]
2020-05-06 Added FTDI placemnt
    [adc.kicad_sch, digitizer_fpga_10b_100MSPS.kicad_pcb, digitizer_fpga_10b_100MSPS.kicad_sch, lna.kicad_sch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]
2020-05-06 Added MCU placement
    [digitizer_fpga_10b_100MSPS.kicad_pcb, mcu.kicad_sch, usb.kicad_sch]
2020-05-06 Added SRAM placement
    [digitizer_fpga_10b_100MSPS.kicad_pcb]
2020-05-06 Added basic FPGA placement
    [digitizer_fpga_10b_100MSPS.kicad_pcb, digitizer_fpga_10b_100MSPS.kicad_sch, fpga.kicad_sch]
2020-05-06 Added buses that were removed when converting from the old format
    [adc.kicad_sch, digitizer_fpga_10b_100MSPS.kicad_pcb, digitizer_fpga_10b_100MSPS.kicad_sch, fpga.kicad_sch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]
2020-05-07 Added FPGA placement
    [digitizer_fpga_10b_100MSPS.kicad_pcb, fpga.kicad_sch]
2020-05-07 Updated placement
    [digitizer_fpga_10b_100MSPS.kicad_pcb]
2020-05-07 Added some design rules
    [digitizer_fpga_10b_100MSPS.kicad_pcb, fpga.kicad_sch]
2020-05-07 Added support lines for BGA fanout
    [digitizer_fpga_10b_100MSPS.kicad_pcb]
2020-05-08 Created Basic polygons
    [digitizer_fpga_10b_100MSPS.kicad_pcb]
2020-05-08 Added LDO output polygons
    [digitizer_fpga_10b_100MSPS.kicad_pcb]
2020-05-08 Moved FPGA capacitors
    [adc.kicad_sch, digitizer_fpga_10b_100MSPS.kicad_pcb, fpga.kicad_sch, lna.kicad_sch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]
2020-05-08 Changed FPGA via diamertal to 350um
    [digitizer_fpga_10b_100MSPS.kicad_pcb]
2020-05-08 Connected FPGA GND
    [digitizer_fpga_10b_100MSPS.kicad_pcb]
2020-05-08 Added some polygons and connected ADC
    [adc.kicad_sch, digitizer_fpga_10b_100MSPS.kicad_pcb, fpga.kicad_sch, lna.kicad_sch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]
2020-05-08 Added power polygons
    [adc.kicad_sch, digitizer_fpga_10b_100MSPS.kicad_pcb, digitizer_fpga_10b_100MSPS.kicad_sch, fpga.kicad_sch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]
2020-05-08 Updated LDO VCC input polygons
    [digitizer_fpga_10b_100MSPS.kicad_pcb]
2020-05-08 Fixed IN vias
    [digitizer_fpga_10b_100MSPS.kicad_pcb]
2020-05-08 Added power manager layout
    [digitizer_fpga_10b_100MSPS.kicad_pcb]
2020-05-08 Moved some resistors
    [digitizer_fpga_10b_100MSPS.kicad_pcb]
2020-05-09 Added ground polygon on TOP layer
    [digitizer_fpga_10b_100MSPS.kicad_pcb]
2020-05-09 Added part SRAM layout
    [digitizer_fpga_10b_100MSPS.kicad_pcb, fpga.kicad_sch]
2020-05-09 Added part SRAM layout
    [adc.kicad_sch, digitizer_fpga_10b_100MSPS.kicad_pcb, digitizer_fpga_10b_100MSPS.kicad_sch, fpga.kicad_sch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]
2020-05-10 Chenged to 4 layers
    [digitizer_fpga_10b_100MSPS.kicad_pcb]
2020-05-10 Chenged 350um track to 200um
    [digitizer_fpga_10b_100MSPS.kicad_pcb]
2020-05-10 Updated ADC layout
    [digitizer_fpga_10b_100MSPS.kicad_pcb]
2020-05-10 Added some tracks
    [digitizer_fpga_10b_100MSPS.kicad_pcb]
2020-05-11 Changed TP footprint
    [digitizer_fpga_10b_100MSPS.kicad_pcb]
2020-05-11 Moved ADC
    [digitizer_fpga_10b_100MSPS.kicad_pcb]
2020-05-11 Updated FLASH placement
    [digitizer_fpga_10b_100MSPS.kicad_pcb]
2020-05-12 Chenged Rs positions
    [digitizer_fpga_10b_100MSPS.kicad_pcb]
2020-05-12 Added test RAM layout
    [digitizer_fpga_10b_100MSPS.kicad_pcb]
2020-05-12 Added FTDI layout
    [adc.kicad_sch, digitizer_fpga_10b_100MSPS.kicad_pcb, digitizer_fpga_10b_100MSPS.kicad_sch, fpga.kicad_sch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]
2020-05-12 Added MCU power layout
    [digitizer_fpga_10b_100MSPS.kicad_pcb]
2020-05-12 Added LNA layout
    [digitizer_fpga_10b_100MSPS.kicad_pcb]
2020-05-12 Updated some layout
    [digitizer_fpga_10b_100MSPS.kicad_pcb]
2020-05-12 Removed legacy rescue and cashe files
    [adc.kicad_sch, fpga.kicad_sch, mcu.kicad_sch, power.kicad_sch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]
2020-05-13 Updated polygons
    [digitizer_fpga_10b_100MSPS.kicad_pcb]
2020-05-13 Added some layout
    [digitizer_fpga_10b_100MSPS.kicad_pcb]
2020-05-13 Rename buses from X..0 to 0..X
    [adc.kicad_sch, digitizer_fpga_10b_100MSPS.kicad_pcb, digitizer_fpga_10b_100MSPS.kicad_sch, fpga.kicad_sch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]
2020-05-14 Added RAM layout
    [adc.kicad_sch, digitizer_fpga_10b_100MSPS.kicad_pcb, fpga.kicad_sch, mcu.kicad_sch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]
2020-05-14 Updated layout
    [adc.kicad_sch, digitizer_fpga_10b_100MSPS.kicad_pcb, fpga.kicad_sch, mcu.kicad_sch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]
2020-05-14 Created new RAM placement and test layout
    [adc.kicad_sch, digitizer_fpga_10b_100MSPS.kicad_pcb, fpga.kicad_sch, mcu.kicad_sch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]
2020-05-15 Minimalised RAM layout
    [digitizer_fpga_10b_100MSPS.kicad_pcb]
2020-05-15 Aligned RAM vias
    [digitizer_fpga_10b_100MSPS.kicad_pcb]
2020-05-15 Upgraded SRAM layout
    [digitizer_fpga_10b_100MSPS.kicad_pcb]
2020-05-15 Added FPGA LEDs layout
    [adc.kicad_sch, digitizer_fpga_10b_100MSPS.kicad_pcb, digitizer_fpga_10b_100MSPS.kicad_sch, fpga.kicad_sch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]
2020-05-15 Updated FLASH layout
    [digitizer_fpga_10b_100MSPS.kicad_pcb]
2020-05-15 Added MCU LED layout
    [adc.kicad_sch, digitizer_fpga_10b_100MSPS.kicad_pcb, fpga.kicad_sch, mcu.kicad_sch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]
2020-05-15 Updated FPGA LED layout
    [digitizer_fpga_10b_100MSPS.kicad_pcb]
2020-05-15 Added SPI connection
    [adc.kicad_sch, digitizer_fpga_10b_100MSPS.kicad_pcb, fpga.kicad_sch, mcu.kicad_sch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]
2020-05-15 Added bridge connection
    [digitizer_fpga_10b_100MSPS.kicad_pcb, fpga.kicad_sch, mcu.kicad_sch]
2020-05-15 Added USB layout
    [digitizer_fpga_10b_100MSPS.kicad_pcb]
2020-05-15 Added clock layout
    [digitizer_fpga_10b_100MSPS.kicad_pcb]
2020-05-15 Added SWD layout
    [digitizer_fpga_10b_100MSPS.kicad_pcb]
2020-05-15 Added some power layout
    [digitizer_fpga_10b_100MSPS.kicad_pcb]
2020-05-15 Connected reset to FPGA
    [digitizer_fpga_10b_100MSPS.kicad_pcb]
2020-05-15 Connected FPGA controll
    [digitizer_fpga_10b_100MSPS.kicad_pcb, mcu.kicad_sch, sram.kicad_sch, usb.kicad_sch]
2020-05-15 Connected ADC jumper
    [digitizer_fpga_10b_100MSPS.kicad_pcb]
2020-05-15 Fixed some design rules
    [digitizer_fpga_10b_100MSPS.kicad_pcb]
2020-05-15 Fixed amp test points
    [digitizer_fpga_10b_100MSPS.kicad_pcb]
2020-05-15 Updated polygons and removed redundant BGA fan out
    [digitizer_fpga_10b_100MSPS.kicad_pcb]
2020-05-15 Added vias board round
    [digitizer_fpga_10b_100MSPS.kicad_pcb]
2020-05-15 Small layout update
    [adc.kicad_sch, digitizer_fpga_10b_100MSPS.kicad_pcb, fpga.kicad_sch, lna.kicad_sch]
2020-05-15 Updated power polygons
    [digitizer_fpga_10b_100MSPS.kicad_pcb]
2020-05-16 Refactored FPGA schematic
    [adc.kicad_sch, digitizer_fpga_10b_100MSPS.kicad_pcb, digitizer_fpga_10b_100MSPS.kicad_sch, fpga.kicad_sch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]
2020-05-17 Added external oscilator for FPGA and ADC to schematic
    [adc.kicad_sch, digitizer_fpga_10b_100MSPS.kicad_sch, lna.kicad_sch, mcu.kicad_sch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]
2020-05-17 Added oscilator layout
    [adc.kicad_sch, digitizer_fpga_10b_100MSPS.kicad_pcb, digitizer_fpga_10b_100MSPS.kicad_sch, fpga.kicad_sch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]
2020-05-18 Added FTDI RST support
    [adc.kicad_sch, digitizer_fpga_10b_100MSPS.kicad_pcb, digitizer_fpga_10b_100MSPS.kicad_sch, fpga.kicad_sch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]
2020-05-18 Fixed MCU RST
    [adc.kicad_sch, digitizer_fpga_10b_100MSPS.kicad_pcb, digitizer_fpga_10b_100MSPS.kicad_sch, fpga.kicad_sch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]
2020-05-18 Updated RST layout
    [digitizer_fpga_10b_100MSPS.kicad_pcb]
2020-05-19 Added some layout updated
    [digitizer_fpga_10b_100MSPS.kicad_pcb]
2020-05-19 Removed LNA test points
    [digitizer_fpga_10b_100MSPS.kicad_sch, lna.kicad_sch, power.kicad_sch]
2020-05-19 Added bypass C to RST gate
    [digitizer_fpga_10b_100MSPS.kicad_pcb, digitizer_fpga_10b_100MSPS.kicad_sch, usb.kicad_sch]
2020-05-19 Updated SPI layout
    [digitizer_fpga_10b_100MSPS.kicad_pcb]
2020-05-19 Reannoted schematic
    [digitizer_fpga_10b_100MSPS.kicad_pcb]
2020-05-19 Updated F.SilkS
    [digitizer_fpga_10b_100MSPS.kicad_pcb]
2020-05-19 Added LEDs text to F.SilkS
    [digitizer_fpga_10b_100MSPS.kicad_pcb]
2020-05-19 Added connectors description to F.SilkS
    [digitizer_fpga_10b_100MSPS.kicad_pcb]
2020-05-19 Added logo and description to F.Silks
    [adc.kicad_sch, digitizer_fpga_10b_100MSPS.kicad_pcb, digitizer_fpga_10b_100MSPS.kicad_sch, fpga.kicad_sch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]
2020-05-19 Aligned text to B.SilkS
    [digitizer_fpga_10b_100MSPS.kicad_pcb]
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2020-06-30 Fixed ADC PWRDN problem
    [adc.kicad_sch, digitizer_fpga_10b_100MSPS.kicad_pcb, digitizer_fpga_10b_100MSPS.kicad_sch, fpga.kicad_sch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]
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2020-08-16 Fixed netclass
    [digitizer_fpga_10b_100MSPS.kicad_pcb]
2020-08-17 Fixed project for new ID access in KiCad V6
    [digitizer_fpga_10b_100MSPS.kicad_pcb]
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2021-01-17 Fixed 3D path for KiCad V6
    [digitizer_fpga_10b_100MSPS.kicad_pcb]
2021-01-17 Fixed SCH file format
    [adc.kicad_sch, digitizer_fpga_10b_100MSPS.kicad_sch, fpga.kicad_sch, lna.kicad_sch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]
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
